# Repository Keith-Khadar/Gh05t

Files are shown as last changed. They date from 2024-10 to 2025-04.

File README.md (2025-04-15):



# Project Overview

This project aims to design and develop a wearable EEG headset with an integrated data acquisition system. Using OpenBCI Ultracortex Mark IV as a template, the headset is designed to map the electrodes according to the 10-20 system. We expand on this design by integrating our own 3D printed or button-snap electrodes for enhanced modularity. Additionally, we investigate various EEG data acquistion hardware options, varying in cost, precision, and usability, to enhance accessibility and modularity in EEG systems - ranging from off-the-shelf hardware to custom-designed PCBs and circuit designs. The hardware will communicate with a computer for analysis by a machine learning (ML) model to detect gestures or possible speech, with the possibility of integration into Virtual-Reality (VR) applications. Lastly, the system will feature a custom GUI, enabling users to visualize EEG data in real-time from the various custom hardware configurations we explore.

We provide various levels to users depending on cost, precision, and usability:

| Feature                     | High Performance Development Board[^1]    | Balanced Performance Board[^2]                | Low Cost EEG Filtering Circuit[^3]            |
| --------------------------- | ----------------------------------------- | --------------------------------------------- | --------------------------------------------- |
| **Number of Channels**      | 8\*                                       | 8\*                                           | 8                                             |
| **Resolution**              | 24-bit                                    | 24-bit                                        | 12-bit                                        |
| **Typical Sampling Rate**   | 250 Hz                                    | 250 Hz                                        | <33 Hz                                        |
| **ADC Chip**                | ADS1299-IPAG                              | ADS1299-IPAG                                  | Internal RPi Pico ADC                         |
| **Board**                   | EEG Development Board with ESP32-S3       | Custom PCB                                    | Custom breadboard/featherboard circuit        |
| **Microcontroller**         | XIAO ESP32-C6                             | DFRobot Firebeetle ESP32 32D                  | Raspberry Pi Pico W                           |
| **Connectivity**            | USB-C/Bluetooth/WiFi                      | Micro-USB/Bluetooth/WiFi                      | Micro-USB/WiFi                                |
| **Power Source**            | Battery/USB                               | Battery/USB                                   | Battery/USB                                   |
| **Battery Life**            | 8 hours                                   | -                                             | <1 hour                                       |
| **GUI Support**             | OpenBCI GUI                               | Custom GUI                                    | Custom GUI                                    |
| **Form Factor**             | Button Snap Electrodes w/ OpenBCI Headset | 3D printed Claw Electrodes w/ OpenBCI Headset | 3D printed Claw Electrodes w/ Custom Headband |
| **Communication Protocols** | SPI, ESPNOW, UART                         | SPI, BLE                                      | UDP WebSocket                                 |
| **Price**                   | ~$375                                     | ~$100                                         | ~$50                                          |

\* The ADS1299 has the capabilities to daisy chain, therefore expanding the channel number from 8 to 16 but it is not fully implemented on the custom PCB. Refer to the ADS1299 PCB folder for additional information.

[^1]: Refer to [High_Performance\README.md](https://github.com/Keith-Khadar/Gh05t/tree/main/High_Performance) for more information on the setup and specifics for the system.
[^2]: Refer to [Balanced_Performance\README.md](https://github.com/Keith-Khadar/Gh05t/tree/main/Balanced_Performance) for more information on the setup and specifics for the system.
[^3]: Refer to [Low_Cost\README.md](https://github.com/Keith-Khadar/Gh05t/tree/main/Low_Cost) for more information on the setup and specifics for the system.

## Completed Work/In Progress for Milestone Production Release

-   **Working Balanced Performance Pipeline (ADS1299 Breakout PCB)**: Eye blinks were detected successfully in the FFT and Time Series plots but was unable to receive consistent and robust results after each trial.
    -   Work in progress of doing trial and error to reproduce results.
-   **Housing Design for Balanced Performance Board (Breakout PCB)**: A CAD design of a housing unit for the ADS1299 Breakout PCB was completed.
-   **Receiver code optimization for the High Performance board**: The receiver code was optimized for better efficiency on the high-performance board by restructuring logic, minimizing redundant operations, and improving resource utilization.
-   **Optimizing Real Time Reading on the GUI**: Since eye blinks were successfully shown in the time series, the SDED, with the calibration of the delta and alpha variables, was able to successfully label with minimal latency the sample positions where the blinking occurred.
-   **EEG Game Application**: In order to expand the application of using the EEG data and detecting events like eye blinking, a VR and simple blinking game was created. A WebSocket host was created in the GUI and successfully broadcasts the SDED labels to any client to act as a controller for a game.
-   **Signal Preprocessing** : The EEG signal preprocessing pipeline is fully implemented, ensuring artifact removal, filtering, and independent component extraction before further processing. FastICA, InfoMax, NLMS and VSS-APA are implemented to extract information components from raw EEG signals in real-time.
-   **Event Detection/Prediction Model**: The EEG-based event detection pipeline and machine learning models have been developed to analyze real-time brain activity and infer motor function. NLMS, Batch-Wiener Filter and VSS-APA have been implemeted for predictions - Statistical Deviation Event Detection Model and Information Theoretic Learning Point Process Detection Models have been implemented for more sophisticed event flagging.

# Project Architecture

### <p align="center">**High Performance Development Board**[^1]</p>

| <div style="width:400px">Hardware Architecture & Wiring</div>  | Components  | Communication Protocols  |
| ----------------------- | ----------------------- | ----------------------- |
| High Performance Board | - OpenBCI 3D Headset Design<br> - Depth-adjustable spring loaded 3D printed assembly with metal snap electrodes provides good signal strength for EEG signals <br> - EEG ESP Development Board with ESP32-S3 <br> - XIAO ESP32-C6<br> - Protective case for the development board<br> | - SPI communication between ADS1299 chip and ESP32-S3<br> - ESP-NOW WiFi data transmission between Development Board and ESP32-C6<br> - UART serialized data transmission through USB-C connection between ESP32-C6 and computer receiver <br> |

-   **Software**
    -   Once the ESP32-C6 captures the incoming EEG data from the ESP32-S3, the UART data is captured through a python script and written to a file. The captured EEG data in this file can be viewed using OpenBCI GUI. The EEG data in this file will be feed to the machine learning model to draw inferences after analysis of the data.
    -   A python script is employed to label and timestamp the 8-channel EEG blinking data. This script facilitates the real-time processing and organization of the data, ensuring that each blink event is accurately marked with its corresponding timestamp for subsequent analysis.
    -   An end-to-end high-performance EEG pipeline leverages an ESP32 EEG board and ESP32-C6 to wirelessly transmit 8-channel, ultra-low-noise data at 250 samples/sec via ESP-NOW, enabling real-time processing in Python and visualization through OpenBCI GUI or a custom interface.
    <p align="center">
    data collection stages
    fft plot
    </p>

### <p align="center">**Balanced Performance Board**[^2]</p>

| <div style="width:450px">Hardware Architecture & Wiring</div>  | Components  | Communication |
| ----------------------- | ----------------------- | ----------------------- |
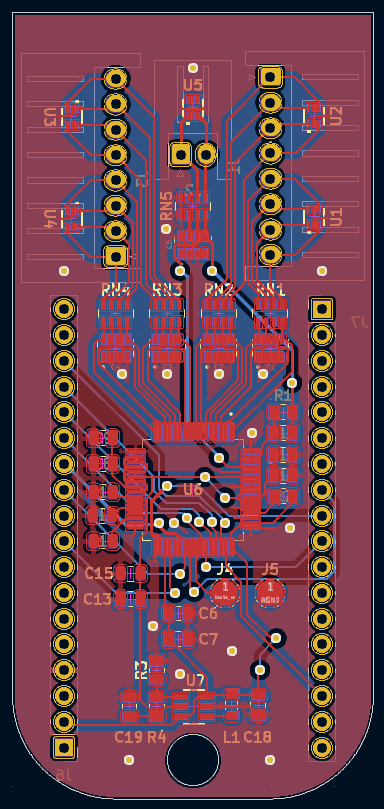
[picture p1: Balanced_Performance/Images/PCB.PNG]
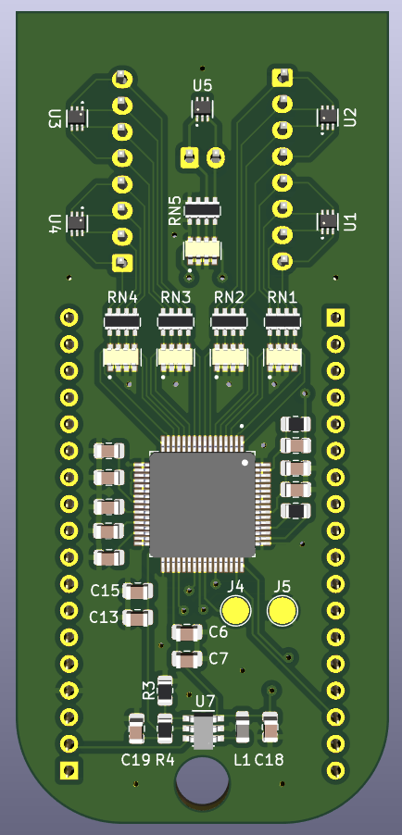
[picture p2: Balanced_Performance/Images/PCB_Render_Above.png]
|    | - OpenBCI 3D Headset Design<br> - 3D Printed Claw Electrodes<br> - Custom ADS1299 PCB<br> - DFRobot Firebeetle ESP32 32D <br> | - SPI communication between the ADS1299 PCB and Firebeetle ESP32 <br> - BLE data transmission between the Firebeetle ESP32 and computer receiver <br> |

-   **Software**
    -   Once the Firebeetle ESP32 is supplied power, the BLE server is turned on and ready to transmit data to any device that connects to the server. The **GH05T GUI** is used to connect to the BLE server and read incoming real-time data.

### <p align="center">**Low Cost Filtering Circuit**[^3]</p>

| <div style="width:500px">Hardware Architecture & Wiring</div>   | Components | Communication Protocols |
| ----------------------- | ----------------------- | ----------------------- |
|  | - Custom Filtering and Component Circuit on breadboard/featherboard <br> - Raspberry Pi Pico W <br> | - TCP WebSocket data transmission between Raspberry Pi Pico W and computer receiver |

-   **Software**
    -   Once the Raspberry Pi Pico W is supplied power,UDP WebSocket is opened and transmits data to any device that connects to the server. The **GH05T GUI** is used to connect to the WebSocket server and read incoming real-time data.

### <p align="center">**GH05T Graphic User Interface**[^4]</p>

| <div style="width:300px">Function and Feature Architecture</div> | Visuals/GUI  |
| ----------------| ---------------------- |
| GUI Flow | GUI Flow [PyQt](https://doc.qt.io/qtforpython-6/) & [Matplotlib](https://matplotlib.org/): Widget and EEG Data Visualization |

[^4]: Refer to [Gh05t GUI\README.md](https://github.com/Keith-Khadar/Gh05t/tree/main/Gh05t%20GUI) for more information on the setup and specifics on the GUI.

### <p align="center">**Signal Processing and Machine Learning**[^5]</p>

-   **EEG Signal Pre-processing**:

    -   Format:
        -   Input: Raw 4 channel electrode data
        -   Output: K-Independent Signals (Components)
    -   Processing Options:
        -   FastICA , NLMS: Fast Inference
        -   InfoMax or VSS-APA: Versatility & Robustness

-   **EEG Signal Machine Learning**:
    -   Format:
        -   Input: K-Independent Signals (Components)
        -   Output: User Defined Target Output
    -   Target:
        -   User Defined Target Desired Output, i.e. eye activity or motion.
    -   Model:
        -   Structure: Artifical Neural Network (Regressor)
        -   Pre-Training: PCA-Pretraining for optimal features
        -   Training: Network Tuning based on Target Data

[^5]: Refer to [Machine_Learning\README.md](https://github.com/Keith-Khadar/Gh05t/tree/main/Machine_Learning) for more information on the setup and specifics.

## Known Bugs

- The Balanced Performance Board ADS1299 completely stopped working after trying to fit the casing to the hardware. This was an unexpected issue that is not able to be understood. Possible issues that could have occurred for the chip to completely stop working is somehow the chip received a surge of power that could have damaged it. 

## Difficulties/Challenges

-   **3D Printing Fail**: Weak legs on 3D electrodes
    -   The initial model found and used for the electrodes has spindly legs. In combination with two snaps of the filament during printing, the legs were incredibly weak and many snapped during removal from the print bed.
    -   Fix: Load filament onto spool to eliminate snapping during print. Custom design electrodes with filleted legs to enhance their strength. Increase the number of walls when slicing model for printing.
    -   Above fix solved combined with printing on a higher quality printer and in a different orientation fixed the issues.
-   **Snap Plating**: Purchased snaps are covered in non-conductive coating
    -   Prevented soldering, but can be scrapped off with a knife.
    -   Reduces signal integritty of electrodes.
    -   Fix: Looking into alternative unplated snap connectors.
    -   Above fix solves the issue in initial testing. Will continue to monitor as further testing is conducted.
-   **Inaccurate EEG Data**: Data recorded during initial testing is inaccurate.
    -   The poor quality electrodes(see snap plating challenge & 3d printing fail) as well as the ADC optimized for Electromyography (EMG) data recording instead of the use case of Electroencephalography (EEG), resulted in poor quality data.
    -   Fix: Custom designed PCB breakout board for the ADS1299 which is designed for EEG data acquisition.
-   **GUI Real Time Data**: Optimizing the timing between data conversion from the ADS1299 to the GUI has introduced latency.
    -   Fix: Utilizing threading and precise timing between frame updating and loading.
-   **ADS1299 Electrode Setup**: Setting up the registers for specific BIAS, SRB1/2, and Electrode connections proved difficult with our system. This was causing reading alpha waves to be difficult.
    -   Fix: Using the SRB1, connected to the earlobe/mastoid, routed to all the negative parts of the electrode channels for reference. Using the BIAS, also connected to the earlobe/mastoid, routed to the postive electrode channels for signal derivation.

## License

## Contact

## Acknowledgements

We would like to extend our gratitude to OpenBCI for having open source repositories with headset designs, ADS1299 libraries, and user interface code. These repositories played a significant role in the success of the project!

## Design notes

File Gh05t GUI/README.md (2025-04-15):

# Real-Time EEG Visualization GUI
## Overview

The Graphic User Interface (GUI) is a Python-based real-time visualization tool for viewing multi-channel EEG data over Bluetooth from an ESP32 microcontroller. 

#### Features

- **Real-Time Data Visualization**: Plots live EEG data for multitude of channels in various formats: time, polar fft, and fft.
- **Various forms of data input**: The user has multiple data input options, allowing them flexibility to use various types of hardware.
- **Read Pre-recorded files**: The GUI supports edf and csv.
- **Customizable GUI**: Easy to adapt for additional features like saving data or adjusting plot parameters.
- **Export files**: Can export the incoming data.

#### Dependencies
1. **Hardware** (Optional)
    - **ADS1299 PCB**: Navigate to the esp32 folder, ```esp32\README.md```, for specific setup instructions for Firebeetle ESP32.
    - **Low Cost**: Navigate to the Low Cost folder, ```rpi_low_cost\gh0st\README.md```, for specific setup instructions for the RPi Pico W.
2. **Software**
    - Python 3.7+
    - Bluetooth support on host computer
3. **Libraries**
    - Refer to ```requirements.txt``` to install supporting Python libraries

## Setup Instructions

#### 1. Install Dependencies
Using the ```requirements.txt```, install the library dependencies required for the GUI to run for your environment.

#### 2. Run the GUI
Run the main script to start the GUI. The python script will scan for bluetooth devices automatically when the option is selected.

```bash
python main.py
```

#### 3*. (Optional) Connect to WebSocket Host
The GUI automatically opens the WebSocket at start up. It only broadcasts labels, which requires the user to enable the manual or ML labeling in order to start broadcasting the information. The WebSocket URL is shown to the user next to the Data Input button (the IP4 Addr of the local machine with the PORT number).

The WebSocket broadcasts the labels for the benefit of external applications. For more information, refer to ```Applications``` folder in the repository.

## Code Architecture

- **`main.py`**: Main script for the GUI.
- **`utils/`**: Folder containing all the helper classes and functions.
  - **`ble_handler_.py`**: Creates client to recieve incoming information from the ESP32 BLE server.
  - **`file_handler.py`**: Handles the file uploading, handling, and exporting for data. 
  - **`plot_manager.py`**: Plots various types of Graphs specified by the user.
  - **`signal_processing.py`**: Creates filters and applies signal processing to incoming data.
  - **`websocket_handler.py`**: Handles the websocket communication for the low cost hardware data input. 
- **`resource/`**: Contains any png or supporting files for the GUI
- **`example_eeg_data/`**: Includes eeg data that can be used to test the visualizer.
- **`data/`**: Holds the binary folder where the incoming data will be stored before export. Additionally can be a folder to hold an exported data files.
- **`test/`**: Contains all the unit testing for the GUI.
- **`requirements.txt`**: List of required Python libraries.

## GUI Navigation
The user first must specify how they are inputting data to be read. There are four options to the user for inputting data:
- **ADS1299 PCB**: This is if the user created their own PCB with the ADS1299 chip which communicates to a DFRobot Firebeetle ESP32 development board and sends the data via BLE.
- **Low Cost**: This is if the user does not have the ADS1299 and creates their own low cost breadboard/featherboard circuit that uses an external 12-bit ADC to communicate with the DFRobot Firebeetle ESP32 development to send data over BLE.
- **File Import**: If the user has no hardware to interface with, file import is supported for type .edf.



Once the data is imported, the user has the ability to add and remove plots from the visual. They can play or stop the incoming data stream to look closer at the plots. Additionally, there is a button to allow the user to export the data if they want to create a local file on their machine with the incoming data stream.

## Troubleshooting/Known Bugs
- None.

## Future Work
- The GUI can currently only read from .edf files when uploading. Future work would include expanding the capabilities to .dat and .txt files. 
- Add the ability to scrub through the data on a timeline.
- Package the GUI into a single .EXE once completed with features. This will be done with PyInstaller.

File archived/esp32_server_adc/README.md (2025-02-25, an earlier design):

# README for esp32_server_adc.ino
This project demonstrates a BLE (Bluetooth Low Energy) server application on the ESP32-C6 that reads analog data from a sensor connected to the `A0` pin and broadcasts 
the data to the connected BLE client (mobile phone). The server updates the BLE characteristic every 2 seconds, allowing connected device to retrieve the real-time 
analog value.

## Features
- Uses BLE to broadcast sensor data.
- Reads analog data from pin `A0` with a 12-bit resolution.
- Uses `nRF Connect` for viewing BLE data on mobile.

## Requirements
- **Hardware**: ESP32-C6 board
- **Software**: 
  - Arduino IDE with ESP32 board support
  - ESP32 BLE library (compatible with ESP32-C6)
  - Download nRFConnect app on the phone

## Setup Instructions
1. **Setting up ESP32 board option in the Arduino IDE** 
   - Open Preferences: Go to "File > Preferences" in the Arduino IDE. 
   - Add Board Manager URL: In the "Additional Board Manager URLs" field, paste the ESP32 URL 
     (usually "https://espressif.github.io/arduino-esp32/package_esp32_index.json"). 
   - Open Boards Manager: Navigate to "Tools > Board > Boards Manager". 
   - Install ESP32: Search for "ESP32" and click "Install" for the "ESP32 by Espressif Systems" option. 

2. **Open in Arduino IDE**
   - Open the `esp32_server_adc.ino` file in Arduino IDE.

3. **Upload the Code**
   - Connect your ESP32-C6 board via USB.
   - Click on the upload button to flash the code to the board.

## Code Overview
- **UUID Definitions**: Unique identifiers are used for the BLE service and characteristic.
- **Analog Pin**: Reads data from `A0` and sends it over BLE.
- **BLE Setup**:
  - Initializes BLE with the device name "XIAO_ESP32C6".
  - Creates a BLE server and starts a service with read and write properties.
  - The characteristic is updated with the analog sensor data every 2 seconds.

## BLE Structure

| Parameter      | Value                                    |
|----------------|------------------------------------------|
| **Service UUID**        | `4fafc201-1fb5-459e-8fcc-c5c9c331914b` |
| **Characteristic UUID** | `beb5483e-36e1-4688-b7f5-ea07361b26a8` |

For specific details, please refer to inline comments.

## Usage
1. After flashing, the ESP32-C6 will begin advertising.
2. Use the nRF Connect app to scan for devices.
3. Connect to `XIAO_ESP32C6`.
4. Read the characteristic value to view the analog data.

## Example Output
On connection, the BLE client will receive the analog values every 2 seconds. 
Sample output on the serial monitor:
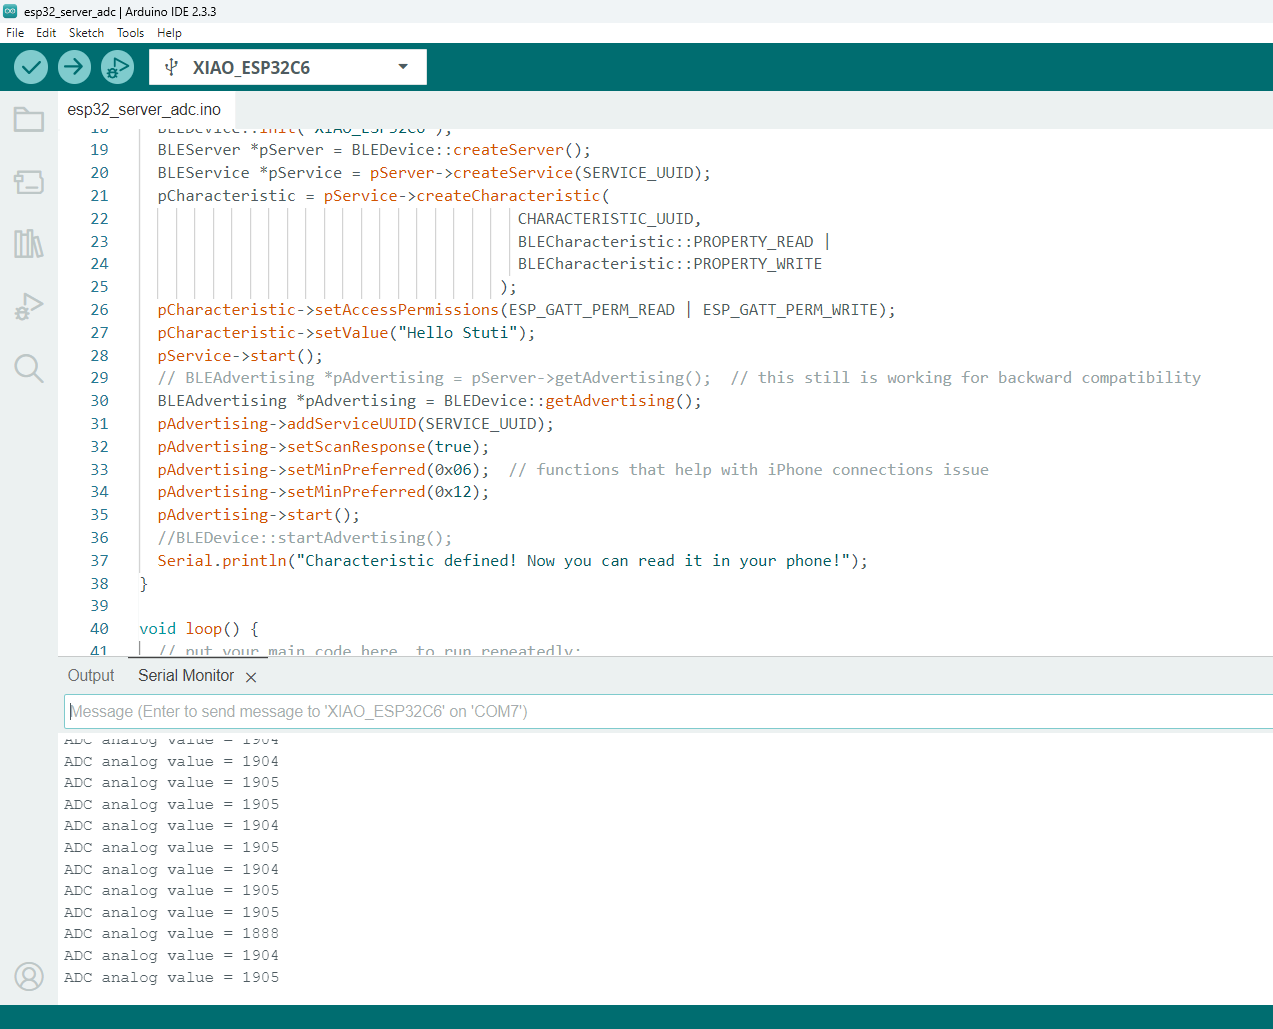
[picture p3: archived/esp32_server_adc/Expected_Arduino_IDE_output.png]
Arduino IDE output


Sample output on the nRF Connect app:<br>
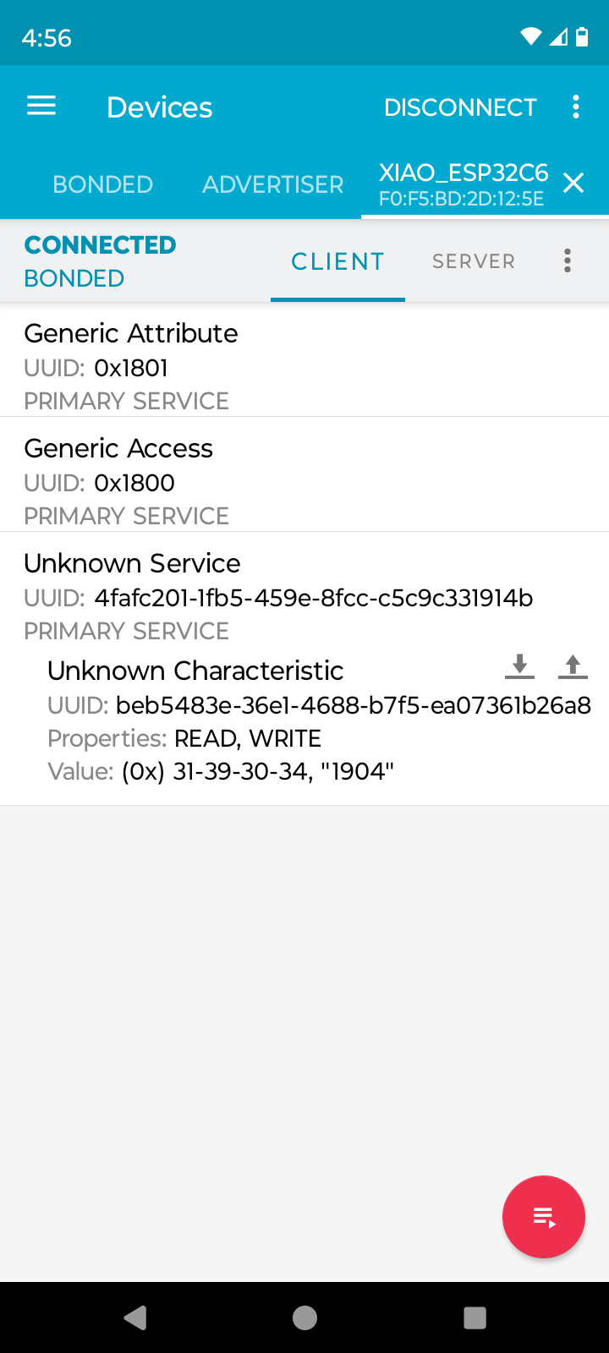
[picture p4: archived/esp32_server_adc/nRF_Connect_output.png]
nRF Connect output


## Mobile Interaction
Since this project utilizes Bluetooth Low Energy (BLE), users need to manually poll the mobile application to retrieve the latest ADC values. 

## Troubleshooting
- Ensure the ESP32-C6 board is selected and it is connected to the correct COM port.
- Check that the correct libraries have been installed in Arduino IDE.

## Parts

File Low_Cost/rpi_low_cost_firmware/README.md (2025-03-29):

# Installation
First you need to install circuit python on your Raspberry Pi Pico. You can do so here at this link: https://circuitpython.org/board/raspberry_pi_pico_w/

# Uploading our code to you Pico
Next you need to upload our code.py into your circuitpy drive that was created from installing circuit python onto your Pico. Afterwards you need to edit/create a settings.toml where you need to include some information.
You need the following information in your settings.toml 'CIRCUITPY_WIFI_SSID', 'CIRCUITPY_WIFI_PASSWORD', 'CIRCUITPY_MULTICAST_GROUP', 'CIRCUITPY_PORT', 'CIRCUITPY_RATE'.

# Using the code
Once you upload the code to the Pico you should be good to go. Now whenever you power the Pico it should create a wifi network with the name and password you specified in the settings.toml.
Once you connect to the wifi it should broadcast data to the ip specified in your mulitcast group and at the port specified in the settings.toml.

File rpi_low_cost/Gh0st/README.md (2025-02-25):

# Raspberry Pi Pico Project
## Overview
This is for the low cost version of the EEG project. It is written in C for the Raspberry Pi Pico. After flashing the firmware onto the Pico, it will output its IP address over serial communication at a baud rate of 115200. From there you can connect using a TCP websocket on port 4242.

## Prerequisites
Raspberry Pi Pico board
C/C++ SDK for the Pico (Raspberry Pi Pico SDK Setup Guide)
CMake (version 3.13 or later)
Make
Serial monitor (e.g., minicom, PuTTY, or Arduino Serial Monitor)
Setup Instructions
## Clone or Download the Code
Download or clone this repository to your local machine.

## Build the Project
Open a terminal and navigate to the project’s root directory:

```bash
cd Gh0st/rpi_low_cost/Gh0st/build
make
```
This will generate a .uf2 file in the build directory.

## Flash the Pico

Hold down the BOOTSEL button on the Pico.
While holding the button, plug the Pico into your computer via USB.
A new mass storage device named RPI-RP2 should appear.
Drag and drop the generated .uf2 file into the RPI-RP2 drive.
Once the file transfer is complete, the Pico will reboot automatically.
View Serial Output
To read the IP address output from the Pico:

Unplug and reconnect the Pico (without holding the BOOTSEL button).
Open your preferred serial monitor and connect to the appropriate port at a baud rate of 115200.
Example using minicom:

```bash
minicom -b 115200 -D /dev/ttyUSB0
(Replace /dev/ttyUSB0 with your actual serial port.)
```
The Pico should display its assigned IP address upon startup.

## Troubleshooting
If the RPI-RP2 drive doesn’t appear, ensure you’re holding the BOOTSEL button while plugging in the Pico.
If no serial output appears, double-check your serial port and baud rate settings.

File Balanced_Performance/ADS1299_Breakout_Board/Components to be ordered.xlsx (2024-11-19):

Component | Quantity (for one board) | Total quantity to be ordered * double the quantity for backup | Ordered? | Links | Price (based on total quantity) | Notes
TPD4E1B06 - Input protection IC | 6 | 24 | F | https://www.digikey.com/en/products/detail/texas-instruments/TPD4E1B06DRLR/4878711 | $8.16
TPS72325 - -2.5V Regulator |  |  |  | https://www.digikey.com/en/products/base-product/texas-instruments/296/TPS72325/23009
TLV700xx - +2.5V Regulator |  |  |  | https://www.digikey.com/en/products/detail/texas-instruments/TLV70033QDDCRQ1/2353662; https://www.mouser.com/c/semiconductors/power-management-ics/voltage-regulators-voltage-controllers/ldo-voltage-regulators/?m=Texas%20Instruments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
MCP1754T-3302E/OT - +3V Regulator |  |  |  | https://www.digikey.com/en/products/detail/microchip-technology/MCP1754T-3302E-OT/2775775; https://www.mouser.com/ProductDetail/Microchip-Technology/MCP1754T-3302E-OT?qs=3wWX5hyYeeTLQCcLPl0MGw%3D%3D
100 uF capacitor | 1 | 10 | F | https://www.digikey.com/en/products/detail/samsung-electro-mechanics/CL21A107MQYNNWE/16615644 | $6.70 | 6.3V rated
10µF capacitor | 1 | 100 | F | https://www.digikey.com/en/products/detail/venkel/C0805X5R100-106KNP-CT/14652235 | $3.84 | 10V rated
1 uF capacitor | 9 | 100 | F | https://www.digikey.com/en/products/detail/venkel/C0805X5R160-105KNE-CT/14651263 | $2.44 | 16V rated
0.1 uF capacitor | 2 | 100 | F | https://www.digikey.com/en/products/detail/venkel/C0805Z5U500-104MNP-CT/14651283 | $1.81 | 50V rated
1 nF capacitor | 1 | 100 | F | https://www.digikey.com/en/products/detail/venkel/C0805X7R250-102KNP-CT/14651672 | 1.81 | 25V rated
1000pF (4 pack) ceramic capacitor | 5 | 50 | F | https://www.digikey.com/en/products/detail/kyocera-avx/W3A45C102K4T2A/9948514 | $6.41 | 50V rated
2.2k (4 pack) resistors | 5 | 50 | F | https://www.digikey.sg/en/products/detail/bourns-inc/CAY16-2201F4LF/2566534 | $1.79
1M resistor | 1 | 100 | F | https://www.digikey.com/en/products/detail/venkel/AGCR0805-RK-1004FT-CT/21345893 | $1.78
Rechargable battery
Crystal oscillator
ADS1299-IPAG | 1 |  | T | https://www.ti.com/product/ADS1299 | $41.58
JST Female connectors 8 Pin |  |  | T | https://www.amazon.com/Kidisoii-Connector-Header-Adapter-XH2-5-DIP-R/dp/B0CXMYPVNL
 |  | https://www.digikey.com/en/products/filter/-capacitors/59 |  |  |  | Link to OpenBCI, Cyton board part list
 |  |  |  |  |  | https://github.com/OpenBCI/V3_Hardware_Design_Files/blob/master/OpenBCI%20Cyton%20Designs/OBCI_Cyton_Plots/OBCI_V4_C%20(Component%20Positions).txt

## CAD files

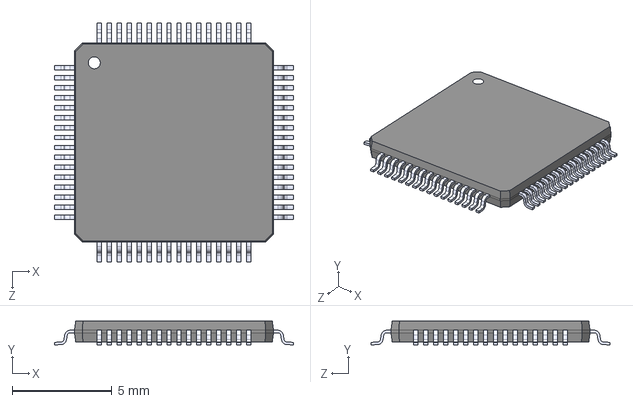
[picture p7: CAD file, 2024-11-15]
Balanced_Performance/ADS1299_Breakout_Board/KiCad_Lib/ADS1299/ADS1299IPAG.step
12.0 x 1.20 x 12.0 mm

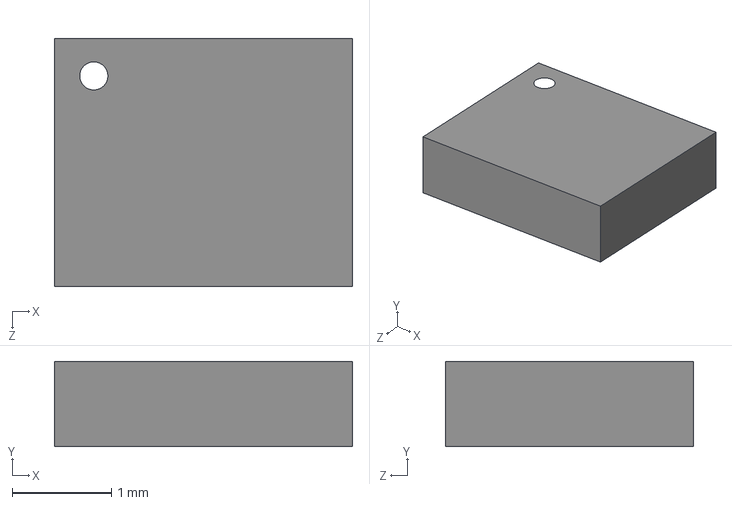
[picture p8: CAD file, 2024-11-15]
Balanced_Performance/ADS1299_Breakout_Board/KiCad_Lib/LSM6DSOX/LSM6DSOX.step
3.00 x 0.86 x 2.50 mm

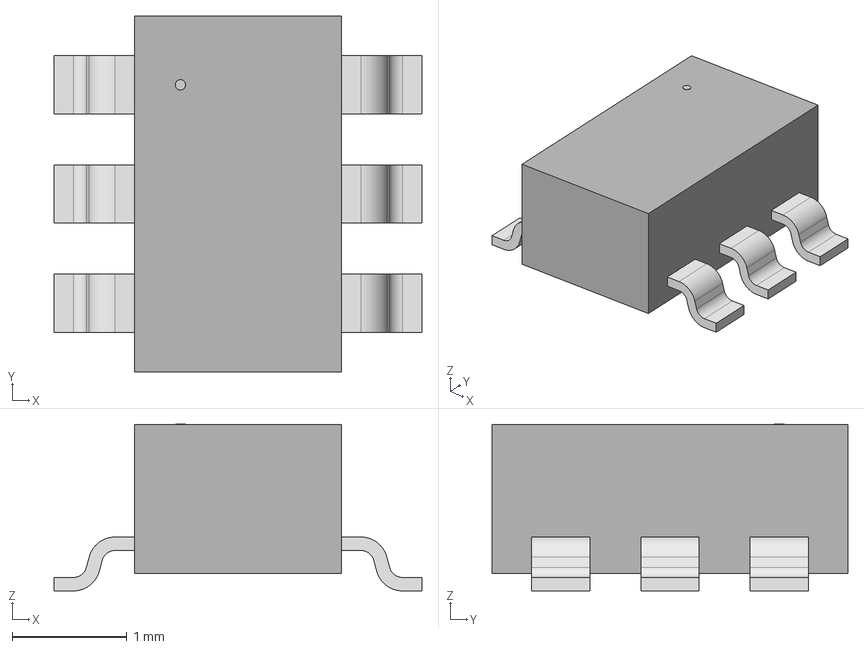
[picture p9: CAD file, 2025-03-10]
Balanced_Performance/Balanced_PCB/ProjectLibraries/MCP1640/MCP1640.step
3.20 x 3.10 x 1.45 mm

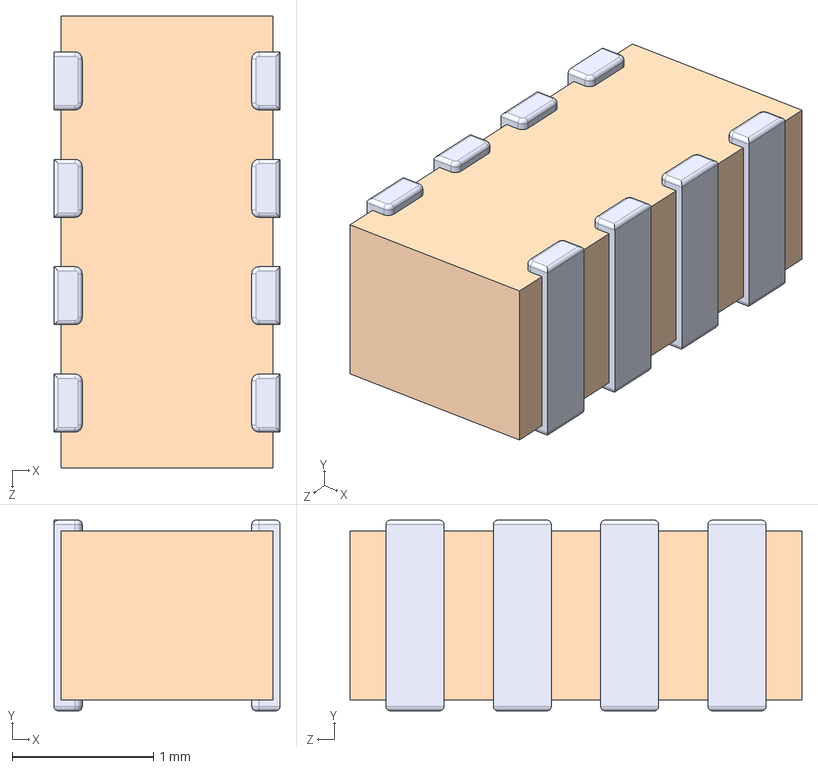
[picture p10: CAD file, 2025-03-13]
Balanced_Performance/Balanced_PCB/ProjectLibraries/W3A45C102K4T2A/W3A45C102K4T2A.step
1.60 x 1.35 x 3.20 mm

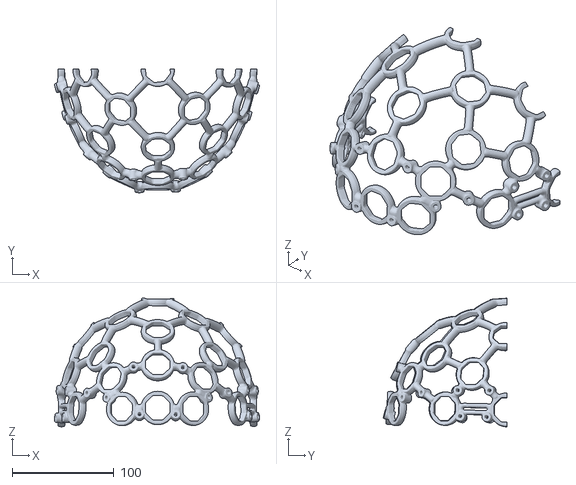
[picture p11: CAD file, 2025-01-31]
Balanced_Performance/CAD/EEG Headset/medium_headset_front_half.stl
201.0 x 121.2 x 126.2

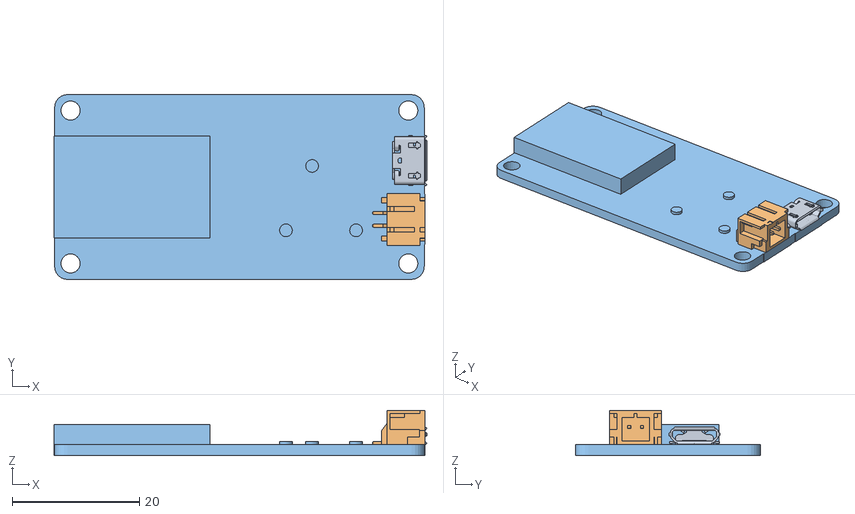
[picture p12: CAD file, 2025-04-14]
Balanced_Performance/CAD/HousingBad/ESP32_Firebeetle_DFR0478V4 v6.obj
58.5 x 29.0 x 7.08
WiFi

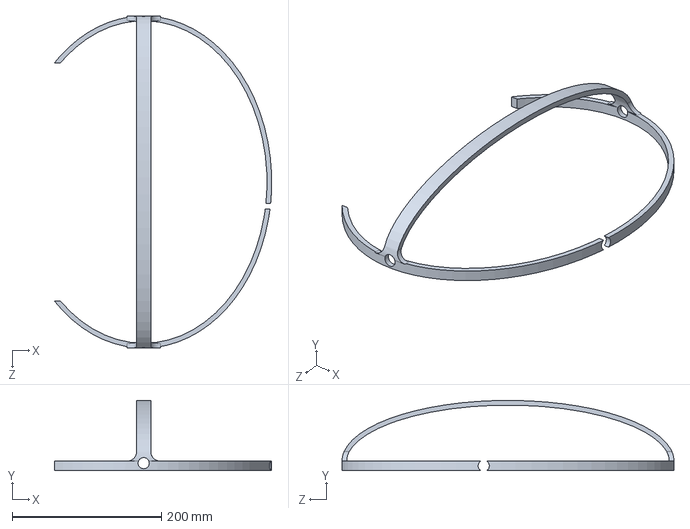
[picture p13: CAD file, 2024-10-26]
hardware/cad/head-mount/proto1.SLDPRT
290.8 x 93.9 x 444.5 mm

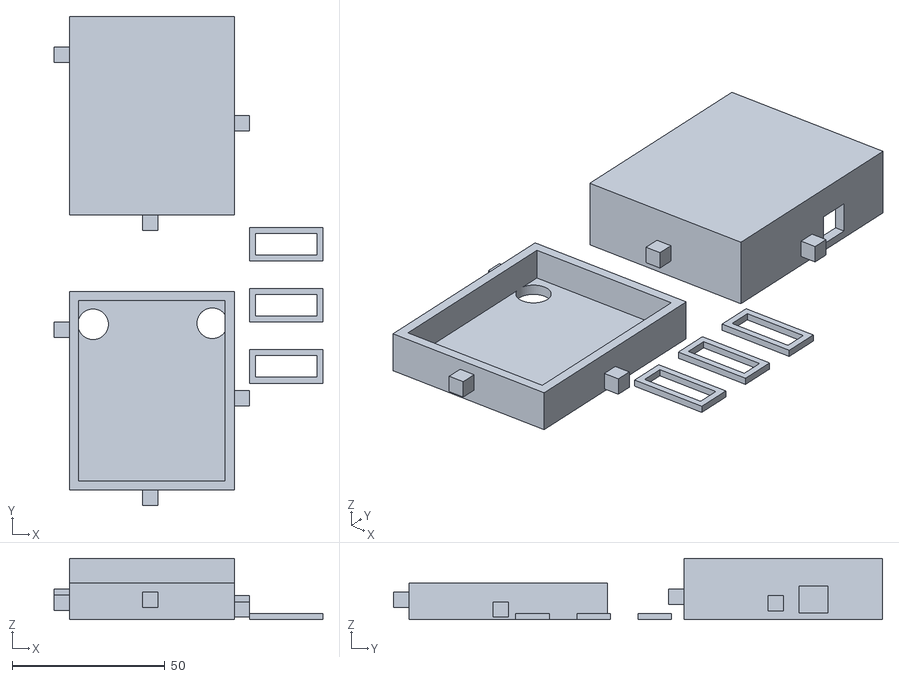
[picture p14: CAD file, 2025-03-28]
High_Performance/CAD/high_performance_board_case.stl
88.0 x 160.0 x 20.0

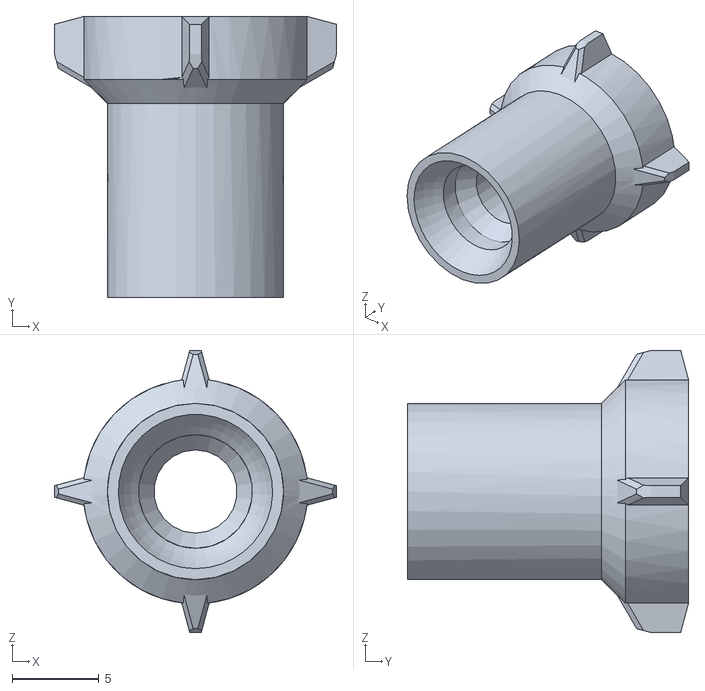
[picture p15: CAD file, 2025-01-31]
Balanced_Performance/CAD/EEG Headset/electrode_holder.STL
16.3 x 16.2 x 16.3

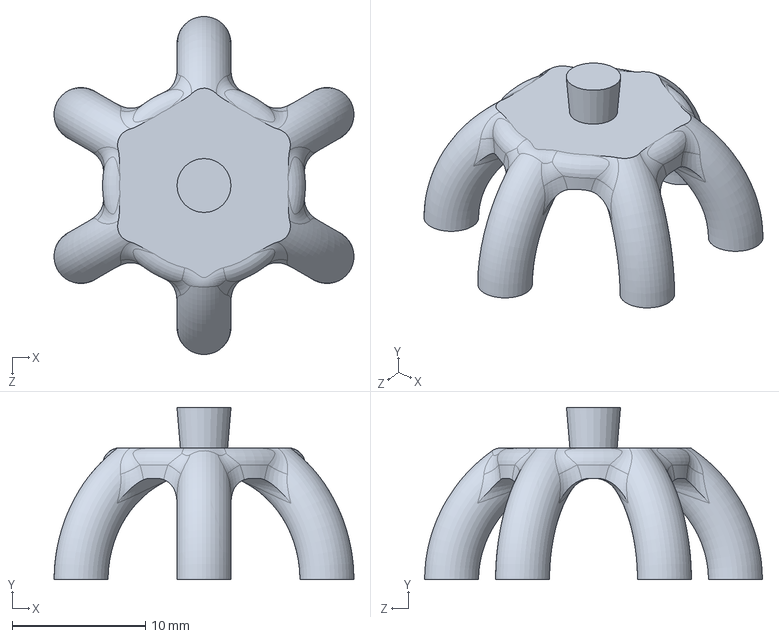
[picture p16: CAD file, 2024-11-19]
Balanced_Performance/CAD/Electrode/electrode.SLDPRT
22.5 x 13.0 x 25.4 mm

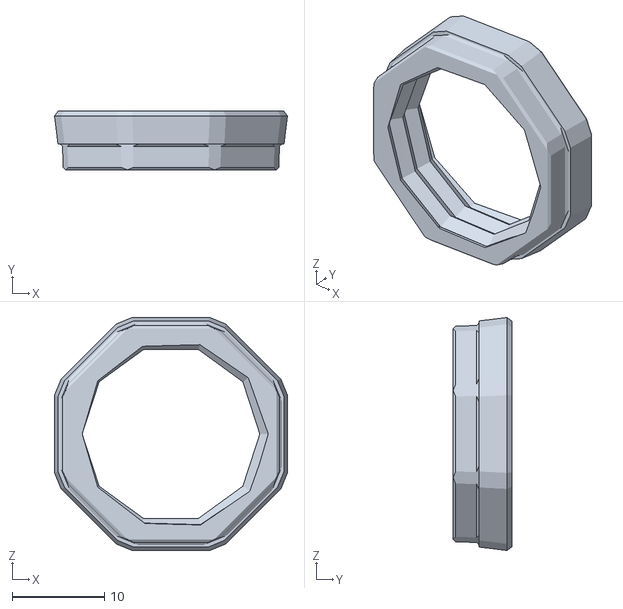
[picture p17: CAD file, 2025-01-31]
Balanced_Performance/CAD/EEG Headset/hexagonal_fitting.STL
25.3 x 6.35 x 25.3

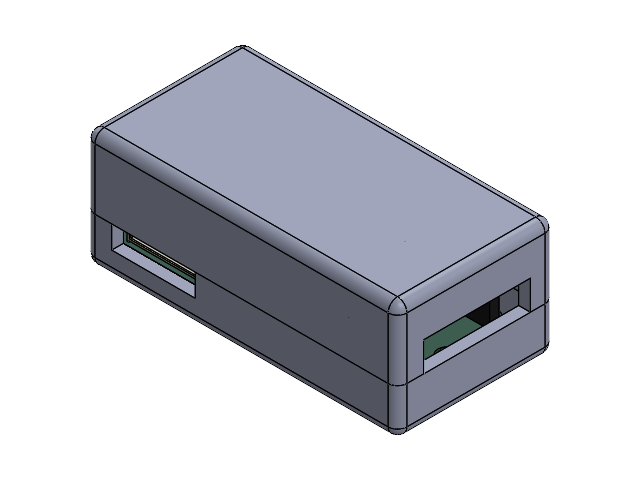
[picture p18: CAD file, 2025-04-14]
Balanced_Performance/CAD/Housing/Balanced_PCB_Housing.SLDASM
Balanced_PCB_Housing
SOT_563.step x 5
C_0805_2012Metric-0.step x 14
W3A45C102KAT2A.step x 5
L_0805_2012Metric-1.step
R_Array_Concave_4x0603-2.step x 5
R_0805_2012Metric-3.step x 4
PAG64.step
part.step
PinSocket_1x18_P2.54mm_Vertical-4.step x 2
JST_S2B_XH_A.step
JST_S8B_XH_A.step x 2
Combined_PCB_PCB.step

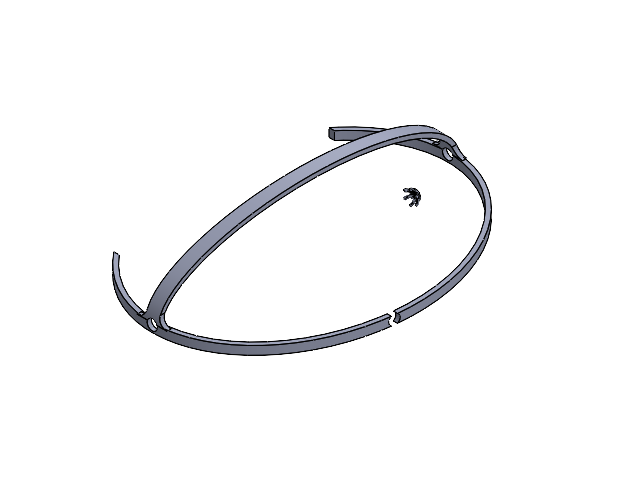
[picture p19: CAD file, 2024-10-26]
hardware/cad/hat.SLDASM
proto1
conductive electrode-short finger-not ours x 2

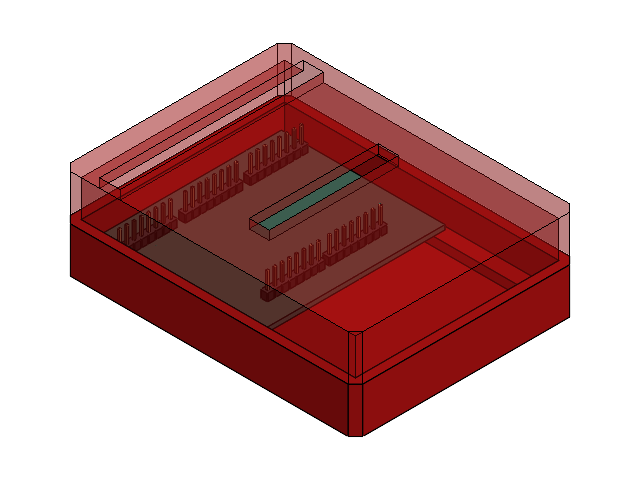
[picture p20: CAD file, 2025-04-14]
Balanced_Performance/CAD/Housing/ADS1299_Breakout_Board_Housing.SLDASM
ADS1299_Breakout_Board_Housing
PinHeader_1x08_P254mm_Vertical.step x 5
ADS1299_Breakout_Board_PCB.step

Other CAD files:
Balanced_Performance/CAD/Electrode/conductive electrode-short finger-not ours.SLDPRT
Balanced_Performance/CAD/HousingBad/ESP32_Firebeetle_DFR0478V4 v7.iges
Balanced_Performance/CAD/EEG Headset/fastening_screw.STL
Balanced_Performance/CAD/EEG Headset/medium_headset_back_half.stl
Balanced_Performance/CAD/EEG Headset/wire_clip.stl
Balanced_Performance/CAD/Electrode/conductive electrode-short finger-not ours.stl
Balanced_Performance/CAD/Electrode/electrode.STL
Balanced_Performance/CAD/Electrode/electrode_screw.SLDPRT
Balanced_Performance/CAD/Electrode/electrode_screw.STL
Balanced_Performance/CAD/Housing/ADS1299_Breakout_Board.SLDASM
Balanced_Performance/CAD/Housing/ADS1299_Breakout_Board.step
Balanced_Performance/CAD/Housing/ADS1299_Breakout_Board_Housing.SLDPRT
Balanced_Performance/CAD/Housing/Balanced_PCB.SLDASM
Balanced_Performance/CAD/Housing/Balanced_PCB.step
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

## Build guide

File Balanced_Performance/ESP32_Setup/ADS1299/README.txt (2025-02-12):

This Library opens communication between ESP32 and the ADS1299
SPI register fuses are directly set to match the ADS1299 interface requirements.
SCK rates: 1MHz, 4MHz, 8MHz. 
All registers and commands are fully accessable.
Here is a list of the functions and parameters available from the Library.

ADS1299.Initialize(int _DRDY, int _RST, int _CS, int _FREQ)
	Data Ready pin, Chip Select pin, and SCK frequency in MHz.
	the current shield uses DRDY = 8; RST 9 CS = 10.
	frequency options are 1MHz, 4MHz, 8MHz.
	bear in mind that at higher frequencies, appropriate delays
	must be taken when sending multiple bytes (DS p.37)
	initialization performs recommended timing and toggle of /RESET pin

//Public Variables

    int DRDY, CS; 		// pin numbers for DRDY and CS 
	These are part of the constructor
	they are not implemented in the current library
	but could be useful in future member functions

    int stat;			// used to hold the status register
	the status register is the first byte returned when you read channel data
	it has 1100 + LOFF_STATP + LOFF_STATN + GPIO[7:4]

    byte regData [24];		// array is used to mirror register data
	this array is used to write multiple locations of ADS register data using WREGS()
	user must first assign target values to the corresponding locations in regData aray
	a call to RREGS() will read multiple locations and update regData array
  
    long channelData [9];	// array used when reading channel data
    boolean verbose;		// turn on/off Serial feedback

//System Commands   

    void WAKEUP();	// wakeup from standby mode
    void STANDBY();	// go into standby mode
    void RESET();	// reset all registers to default values
    void START();	// start a data conversion session
    void STOP();	// stop data conversion

	timed delays are taken where required in the above funcitons. 
	bear in mind the timing of your byte to byte transmission.
	clk on ADS is ~2MHz, so that is a limit.
    
//Data Read Commands

    void RDATAC();	
	enter Read Data Continuous mode
	Read Data Continuous mode enables the ADC and shift registers
	in this mode, you can start a sampling session by setting the start pin,
	or sending the start command

    void SDATAC();	
	enter Stop Read Data Continuous mode
	this mode will let you write and read registers

    void RDATA();	
	Read Data command is used when you're in Stop Read Data Continuous mode
	if you send or set the 'start' command, this allows you to sample on DRDY
	and also have access to read/write the registers. see DS p.37 
    
//Register Read/Write Commands	

    byte getDeviceID();
	simple hello world to check that the device is working properly
	returns 0x3E on the Dev Module I'm using.
	must be in Stop Data Continuous mode prior to sending this

    byte RREG(byte _address);
	returns the value of one register address, specified
	the funcion also updates regData at _address

    void RREGS(byte _address, byte _numRegistersMinusOne);     
	updates the public regData array with current values
	_address is the address to start reading at
	_numRegistersMinusOne is the number of registers to read past the _address
	NOTE: the public regData array behaves like a mirror of the ADS internal arrays,
	however, the user must update the mirror. 

    void printRegisterName(byte _address);
	this is a look up table. part of the verbose feedback and not used external to the library

    void WREG(byte _address, byte _value); 
	writes a single value specified by _value to the register address at _address.

    void WREGS(byte _address, byte _numRegistersMinusOne); 
	writes a number of values to sequential addresses starting at _address
	user must first set values in correct locations of the public byte array regData
	regData is a mirror of the ADS register values

    void printHex(byte _data);
	used to streamline verbose feedback 

    void updateChannelData();
	the public array, channelData[8] gets updated, along with the status register.
	there is bitwise conversion from 3 byte 2's compliment to 4 byte 2's compliment (long)
    
//SPI Transfer function

    byte transfer(byte _data);
	puts the byte _data on the SPI bus, and returns a byte from the SPI bus.

//KNOWN ISSUES

	verbose feedback in the updateChannelData() function bumps against the DRDY signal
	this is because 115200 baud can't keep up?

//USING THIS LIBRARY
	
	The START pin is not broken out. You must send the START() command instead.
	For daisy-chaining in the future, we will route a GPIO to the START pin and 
	header socket.

	You must remeber to get out of Read Data Continuous mode if you want 
	to read/write, and do other register things.

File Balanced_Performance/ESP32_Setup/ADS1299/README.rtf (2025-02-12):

Texas Instruments ADS1299 Arduino Library

This folder contains all work and research for the creation of a software bridge between the Texas Instruments ADS1299 EEG/ECG chip and an Arduino.

Hardware References
[1] ADS1299: http://www.ti.com/product/ads1299
[2] ADS1299 Datasheet: http://www.ti.com/lit/ds/sbas499a/sbas499a.pdf
[3] ADS1299 Analog Evaluation Module: http://www.ti.com/lit/ug/slau443/slau443.pdf

Files
ADS2199.h - Arduino library header file
- contains class methods/variables
ADS1299.cpp - Arduino library cpp file
- contains content of methods and references to the page numbers in the above documents
- current methods:
- WAKEUP()
- STANDBY()
- RESET()
- START()
- STOP()
- RDATAC() - read data continuous
- SDATAC() - stop data continuous
- RDATA()
- RREG()
- WREG()
- transfer() - SPI bit transfer
- updateData() - print data from ADS1299 to serial monitor in Arduino IDE
Definitions.h - Contains all of the variable definitions that are relevant to the ADS1299 chip commands and the SPI communication between the chip and the Arduino.
examples/example_2 - an example arduino sketch that show you how to use the currently implemented methods of the library
keywords.txt - defines the keywords that change color automatically in an arduino sketch using this library

Extra Materials
The "reference" folder contains websites that contain relevant information to the development of the code and also options for electrodes and circuit design of active electrodes and other open-source EEG tools.
Links from meeting with Sean Montgomery (from Sensorstar Labs):
- https://www.olimex.com/Products/EEG/OpenEEG/EEG-ANALOG-ASM/
- https://www.olimex.com/Products/EEG/Electrodes/
- https://www.olimex.com/Products/EEG/Electrodes/EEG-AE/
- https://www.olimex.com/Products/EEG/OpenEEG/EEG-SMT/resources/EEG-SMT-SCHEMATIC-REV-B.pdf
- Sean's Website: http://produceconsumerobot.com/biosensing/
- http://www.saelig.com/miva/merchant.mvc?
- http://www.saelig.com/miva/merchant.mvc?
- http://www.saelig.com/supplier/plessey/PS25255.pdf
- http://ieeexplore.ieee.org/xpl/login.jsp?tp=&arnumber=5598518&url=http%3A%2F%2Fieeexplore.ieee.org%2Fxpls%2Fabs_all.jsp%3Farnumber%3D5598518

version 1) developed by Conor Russomanno (6/20/13)

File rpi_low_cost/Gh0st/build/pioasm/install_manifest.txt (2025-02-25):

/home/embedded/pico/Gh0st/build/pioasm-install/pioasm/pioasm
/home/embedded/pico/Gh0st/build/pioasm-install/pioasm/pioasmTargets.cmake
/home/embedded/pico/Gh0st/build/pioasm-install/pioasm/pioasmTargets-release.cmake
/home/embedded/pico/Gh0st/build/pioasm-install/pioasm/pioasmConfig.cmake
/home/embedded/pico/Gh0st/build/pioasm-install/pioasm/pioasmConfigVersion.cmake

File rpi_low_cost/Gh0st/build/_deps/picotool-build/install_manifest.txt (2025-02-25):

/home/embedded/pico/Gh0st/build/_deps/picotool/picotool
/home/embedded/pico/Gh0st/build/_deps/picotool/picotoolTargets.cmake
/home/embedded/pico/Gh0st/build/_deps/picotool/picotoolTargets-release.cmake
/home/embedded/pico/Gh0st/build/_deps/picotool/picotoolConfig.cmake
/home/embedded/pico/Gh0st/build/_deps/picotool/picotoolConfigVersion.cmake

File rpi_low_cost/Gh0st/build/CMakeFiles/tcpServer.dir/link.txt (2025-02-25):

/usr/bin/arm-none-eabi-g++ -mcpu=cortex-m0plus -mthumb -g -O3 -DNDEBUG -Wl,--build-id=none -Wl,-Map=tcpServer.elf.map --specs=nosys.specs -Wl,--wrap=__clzsi2 -Wl,--wrap=__clzdi2 -Wl,--wrap=__ctzsi2 -Wl,--wrap=__popcountsi2 -Wl,--wrap=__popcountdi2 -Wl,--wrap=__clz -Wl,--wrap=__clzl -Wl,--wrap=__clzll -Wl,--wrap=__ctzdi2 -Wl,--wrap=__aeabi_idiv -Wl,--wrap=__aeabi_idivmod -Wl,--wrap=__aeabi_ldivmod -Wl,--wrap=__aeabi_uidiv -Wl,--wrap=__aeabi_uidivmod -Wl,--wrap=__aeabi_uldivmod -Wl,--wrap=__aeabi_dadd -Wl,--wrap=__aeabi_ddiv -Wl,--wrap=__aeabi_dmul -Wl,--wrap=__aeabi_drsub -Wl,--wrap=__aeabi_dsub -Wl,--wrap=__aeabi_cdcmpeq -Wl,--wrap=__aeabi_cdrcmple -Wl,--wrap=__aeabi_cdcmple -Wl,--wrap=__aeabi_dcmpeq -Wl,--wrap=__aeabi_dcmplt -Wl,--wrap=__aeabi_dcmple -Wl,--wrap=__aeabi_dcmpge -Wl,--wrap=__aeabi_dcmpgt -Wl,--wrap=__aeabi_dcmpun -Wl,--wrap=__aeabi_i2d -Wl,--wrap=__aeabi_l2d -Wl,--wrap=__aeabi_ui2d -Wl,--wrap=__aeabi_ul2d -Wl,--wrap=__aeabi_d2iz -Wl,--wrap=__aeabi_d2lz -Wl,--wrap=__aeabi_d2uiz -Wl,--wrap=__aeabi_d2ulz -Wl,--wrap=__aeabi_d2f -Wl,--wrap=sqrt -Wl,--wrap=cos -Wl,--wrap=sin -Wl,--wrap=tan -Wl,--wrap=atan2 -Wl,--wrap=exp -Wl,--wrap=log -Wl,--wrap=ldexp -Wl,--wrap=copysign -Wl,--wrap=trunc -Wl,--wrap=floor -Wl,--wrap=ceil -Wl,--wrap=round -Wl,--wrap=sincos -Wl,--wrap=asin -Wl,--wrap=acos -Wl,--wrap=atan -Wl,--wrap=sinh -Wl,--wrap=cosh -Wl,--wrap=tanh -Wl,--wrap=asinh -Wl,--wrap=acosh -Wl,--wrap=atanh -Wl,--wrap=exp2 -Wl,--wrap=log2 -Wl,--wrap=exp10 -Wl,--wrap=log10 -Wl,--wrap=pow -Wl,--wrap=powint -Wl,--wrap=hypot -Wl,--wrap=cbrt -Wl,--wrap=fmod -Wl,--wrap=drem -Wl,--wrap=remainder -Wl,--wrap=remquo -Wl,--wrap=expm1 -Wl,--wrap=log1p -Wl,--wrap=fma -Wl,--wrap=__aeabi_lmul -Wl,--wrap=__aeabi_fadd -Wl,--wrap=__aeabi_fdiv -Wl,--wrap=__aeabi_fmul -Wl,--wrap=__aeabi_frsub -Wl,--wrap=__aeabi_fsub -Wl,--wrap=__aeabi_cfcmpeq -Wl,--wrap=__aeabi_cfrcmple -Wl,--wrap=__aeabi_cfcmple -Wl,--wrap=__aeabi_fcmpeq -Wl,--wrap=__aeabi_fcmplt -Wl,--wrap=__aeabi_fcmple -Wl,--wrap=__aeabi_fcmpge -Wl,--wrap=__aeabi_fcmpgt -Wl,--wrap=__aeabi_fcmpun -Wl,--wrap=__aeabi_i2f -Wl,--wrap=__aeabi_l2f -Wl,--wrap=__aeabi_ui2f -Wl,--wrap=__aeabi_ul2f -Wl,--wrap=__aeabi_f2iz -Wl,--wrap=__aeabi_f2lz -Wl,--wrap=__aeabi_f2uiz -Wl,--wrap=__aeabi_f2ulz -Wl,--wrap=__aeabi_f2d -Wl,--wrap=sqrtf -Wl,--wrap=cosf -Wl,--wrap=sinf -Wl,--wrap=tanf -Wl,--wrap=atan2f -Wl,--wrap=expf -Wl,--wrap=logf -Wl,--wrap=ldexpf -Wl,--wrap=copysignf -Wl,--wrap=truncf -Wl,--wrap=floorf -Wl,--wrap=ceilf -Wl,--wrap=roundf -Wl,--wrap=sincosf -Wl,--wrap=asinf -Wl,--wrap=acosf -Wl,--wrap=atanf -Wl,--wrap=sinhf -Wl,--wrap=coshf -Wl,--wrap=tanhf -Wl,--wrap=asinhf -Wl,--wrap=acoshf -Wl,--wrap=atanhf -Wl,--wrap=exp2f -Wl,--wrap=log2f -Wl,--wrap=exp10f -Wl,--wrap=log10f -Wl,--wrap=powf -Wl,--wrap=powintf -Wl,--wrap=hypotf -Wl,--wrap=cbrtf -Wl,--wrap=fmodf -Wl,--wrap=dremf -Wl,--wrap=remainderf -Wl,--wrap=remquof -Wl,--wrap=expm1f -Wl,--wrap=log1pf -Wl,--wrap=fmaf -Wl,--wrap=malloc -Wl,--wrap=calloc -Wl,--wrap=realloc -Wl,--wrap=free -Wl,--wrap=memcpy -Wl,--wrap=memset -Wl,--wrap=__aeabi_memcpy -Wl,--wrap=__aeabi_memset -Wl,--wrap=__aeabi_memcpy4 -Wl,--wrap=__aeabi_memset4 -Wl,--wrap=__aeabi_memcpy8 -Wl,--wrap=__aeabi_memset8 -Wl,-L/home/embedded/pico/Gh0st/build -Wl,--script=/home/embedded/pico/pico-sdk/src/rp2_common/pico_crt0/rp2040/memmap_default.ld -Wl,-z,max-page-size=4096 -Wl,--gc-sections -Wl,--no-warn-rwx-segments -Wl,--wrap=sprintf -Wl,--wrap=snprintf -Wl,--wrap=vsnprintf -Wl,--wrap=printf -Wl,--wrap=vprintf -Wl,--wrap=puts -Wl,--wrap=putchar -Wl,--wrap=getchar CMakeFiles/tcpServer.dir/main.c.o "CMakeFiles/tcpServer.dir/home/embedded/pico/pico-sdk/src/rp2_common/pico_lwip/lwip_nosys.c.o" "CMakeFiles/tcpServer.dir/home/embedded/pico/pico-sdk/src/rp2_common/pico_async_context/async_context_base.c.o" "CMakeFiles/tcpServer.dir/home/embedded/pico/pico-sdk/src/rp2040/pico_platform/platform.c.o" "CMakeFiles/tcpServer.dir/home/embedded/pico/pico-sdk/src/rp2_common/pico_platform_panic/panic.c.o" "CMakeFiles/tcpServer.dir/home/embedded/pico/pico-sdk/src/rp2_common/pico_rand/rand.c.o" "CMakeFiles/tcpServer.dir/home/embedded/pico/pico-sdk/src/rp2_common/pico_unique_id/unique_id.c.o" "CMakeFiles/tcpServer.dir/home/embedded/pico/pico-sdk/src/rp2_common/hardware_flash/flash.c.o" "CMakeFiles/tcpServer.dir/home/embedded/pico/pico-sdk/src/common/hardware_claim/claim.c.o" "CMakeFiles/tcpServer.dir/home/embedded/pico/pico-sdk/src/rp2_common/hardware_sync/sync.c.o" "CMakeFiles/tcpServer.dir/home/embedded/pico/pico-sdk/src/rp2_common/hardware_sync_spin_lock/sync_spin_lock.c.o" "CMakeFiles/tcpServer.dir/home/embedded/pico/pico-sdk/src/rp2_common/pico_bootrom/bootrom.c.o" "CMakeFiles/tcpServer.dir/home/embedded/pico/pico-sdk/src/rp2_common/pico_bootrom/bootrom_lock.c.o" "CMakeFiles/tcpServer.dir/home/embedded/pico/pico-sdk/src/rp2_common/hardware_boot_lock/boot_lock.c.o" "CMakeFiles/tcpServer.dir/home/embedded/pico/pico-sdk/src/rp2_common/pico_flash/flash.c.o" "CMakeFiles/tcpServer.dir/home/embedded/pico/pico-sdk/src/common/pico_time/time.c.o" "CMakeFiles/tcpServer.dir/home/embedded/pico/pico-sdk/src/common/pico_time/timeout_helper.c.o" "CMakeFiles/tcpServer.dir/home/embedded/pico/pico-sdk/src/rp2_common/hardware_timer/timer.c.o" "CMakeFiles/tcpServer.dir/home/embedded/pico/pico-sdk/src/rp2_common/hardware_irq/irq.c.o" "CMakeFiles/tcpServer.dir/home/embedded/pico/pico-sdk/src/rp2_common/hardware_irq/irq_handler_chain.S.o" "CMakeFiles/tcpServer.dir/home/embedded/pico/pico-sdk/src/common/pico_sync/sem.c.o" "CMakeFiles/tcpServer.dir/home/embedded/pico/pico-sdk/src/common/pico_sync/lock_core.c.o" "CMakeFiles/tcpServer.dir/home/embedded/pico/pico-sdk/src/common/pico_sync/mutex.c.o" "CMakeFiles/tcpServer.dir/home/embedded/pico/pico-sdk/src/common/pico_sync/critical_section.c.o" "CMakeFiles/tcpServer.dir/home/embedded/pico/pico-sdk/src/common/pico_util/datetime.c.o" "CMakeFiles/tcpServer.dir/home/embedded/pico/pico-sdk/src/common/pico_util/pheap.c.o" "CMakeFiles/tcpServer.dir/home/embedded/pico/pico-sdk/src/common/pico_util/queue.c.o" "CMakeFiles/tcpServer.dir/home/embedded/pico/pico-sdk/src/rp2_common/hardware_xip_cache/xip_cache.c.o" "CMakeFiles/tcpServer.dir/home/embedded/pico/pico-sdk/src/rp2_common/hardware_clocks/clocks.c.o" "CMakeFiles/tcpServer.dir/home/embedded/pico/pico-sdk/src/rp2_common/hardware_gpio/gpio.c.o" "CMakeFiles/tcpServer.dir/home/embedded/pico/pico-sdk/src/rp2_common/hardware_pll/pll.c.o" "CMakeFiles/tcpServer.dir/home/embedded/pico/pico-sdk/src/rp2_common/hardware_vreg/vreg.c.o" "CMakeFiles/tcpServer.dir/home/embedded/pico/pico-sdk/src/rp2_common/hardware_watchdog/watchdog.c.o" "CMakeFiles/tcpServer.dir/home/embedded/pico/pico-sdk/src/rp2_common/hardware_ticks/ticks.c.o" "CMakeFiles/tcpServer.dir/home/embedded/pico/pico-sdk/src/rp2_common/hardware_xosc/xosc.c.o" "CMakeFiles/tcpServer.dir/home/embedded/pico/pico-sdk/lib/lwip/src/core/init.c.o" "CMakeFiles/tcpServer.dir/home/embedded/pico/pico-sdk/lib/lwip/src/core/def.c.o" "CMakeFiles/tcpServer.dir/home/embedded/pico/pico-sdk/lib/lwip/src/core/dns.c.o" "CMakeFiles/tcpServer.dir/home/embedded/pico/pico-sdk/lib/lwip/src/core/inet_chksum.c.o" "CMakeFiles/tcpServer.dir/home/embedded/pico/pico-sdk/lib/lwip/src/core/ip.c.o" "CMakeFiles/tcpServer.dir/home/embedded/pico/pico-sdk/lib/lwip/src/core/mem.c.o" "CMakeFiles/tcpServer.dir/home/embedded/pico/pico-sdk/lib/lwip/src/core/memp.c.o" "CMakeFiles/tcpServer.dir/home/embedded/pico/pico-sdk/lib/lwip/src/core/netif.c.o" "CMakeFiles/tcpServer.dir/home/embedded/pico/pico-sdk/lib/lwip/src/core/pbuf.c.o" "CMakeFiles/tcpServer.dir/home/embedded/pico/pico-sdk/lib/lwip/src/core/raw.c.o" "CMakeFiles/tcpServer.dir/home/embedded/pico/pico-sdk/lib/lwip/src/core/stats.c.o" "CMakeFiles/tcpServer.dir/home/embedded/pico/pico-sdk/lib/lwip/src/core/sys.c.o" "CMakeFiles/tcpServer.dir/home/embedded/pico/pico-sdk/lib/lwip/src/core/altcp.c.o" "CMakeFiles/tcpServer.dir/home/embedded/pico/pico-sdk/lib/lwip/src/core/altcp_alloc.c.o" "CMakeFiles/tcpServer.dir/home/embedded/pico/pico-sdk/lib/lwip/src/core/altcp_tcp.c.o" "CMakeFiles/tcpServer.dir/home/embedded/pico/pico-sdk/lib/lwip/src/core/tcp.c.o" "CMakeFiles/tcpServer.dir/home/embedded/pico/pico-sdk/lib/lwip/src/core/tcp_in.c.o" "CMakeFiles/tcpServer.dir/home/embedded/pico/pico-sdk/lib/lwip/src/core/tcp_out.c.o" "CMakeFiles/tcpServer.dir/home/embedded/pico/pico-sdk/lib/lwip/src/core/timeouts.c.o" "CMakeFiles/tcpServer.dir/home/embedded/pico/pico-sdk/lib/lwip/src/core/udp.c.o" "CMakeFiles/tcpServer.dir/home/embedded/pico/pico-sdk/lib/lwip/src/core/ipv4/autoip.c.o" "CMakeFiles/tcpServer.dir/home/embedded/pico/pico-sdk/lib/lwip/src/core/ipv4/dhcp.c.o" "CMakeFiles/tcpServer.dir/home/embedded/pico/pico-sdk/lib/lwip/src/core/ipv4/etharp.c.o" "CMakeFiles/tcpServer.dir/home/embedded/pico/pico-sdk/lib/lwip/src/core/ipv4/icmp.c.o" "CMakeFiles/tcpServer.dir/home/embedded/pico/pico-sdk/lib/lwip/src/core/ipv4/igmp.c.o" "CMakeFiles/tcpServer.dir/home/embedded/pico/pico-sdk/lib/lwip/src/core/ipv4/ip4_frag.c.o" "CMakeFiles/tcpServer.dir/home/embedded/pico/pico-sdk/lib/lwip/src/core/ipv4/ip4.c.o" "CMakeFiles/tcpServer.dir/home/embedded/pico/pico-sdk/lib/lwip/src/core/ipv4/ip4_addr.c.o" "CMakeFiles/tcpServer.dir/home/embedded/pico/pico-sdk/lib/lwip/src/core/ipv4/acd.c.o" "CMakeFiles/tcpServer.dir/home/embedded/pico/pico-sdk/lib/lwip/src/core/ipv6/dhcp6.c.o" "CMakeFiles/tcpServer.dir/home/embedded/pico/pico-sdk/lib/lwip/src/core/ipv6/ethip6.c.o" "CMakeFiles/tcpServer.dir/home/embedded/pico/pico-sdk/lib/lwip/src/core/ipv6/icmp6.c.o" "CMakeFiles/tcpServer.dir/home/embedded/pico/pico-sdk/lib/lwip/src/core/ipv6/inet6.c.o" "CMakeFiles/tcpServer.dir/home/embedded/pico/pico-sdk/lib/lwip/src/core/ipv6/ip6.c.o" "CMakeFiles/tcpServer.dir/home/embedded/pico/pico-sdk/lib/lwip/src/core/ipv6/ip6_addr.c.o" "CMakeFiles/tcpServer.dir/home/embedded/pico/pico-sdk/lib/lwip/src/core/ipv6/ip6_frag.c.o" "CMakeFiles/tcpServer.dir/home/embedded/pico/pico-sdk/lib/lwip/src/core/ipv6/mld6.c.o" "CMakeFiles/tcpServer.dir/home/embedded/pico/pico-sdk/lib/lwip/src/core/ipv6/nd6.c.o" "CMakeFiles/tcpServer.dir/home/embedded/pico/pico-sdk/lib/lwip/src/api/api_lib.c.o" "CMakeFiles/tcpServer.dir/home/embedded/pico/pico-sdk/lib/lwip/src/api/api_msg.c.o" "CMakeFiles/tcpServer.dir/home/embedded/pico/pico-sdk/lib/lwip/src/api/err.c.o" "CMakeFiles/tcpServer.dir/home/embedded/pico/pico-sdk/lib/lwip/src/api/if_api.c.o" "CMakeFiles/tcpServer.dir/home/embedded/pico/pico-sdk/lib/lwip/src/api/netbuf.c.o" "CMakeFiles/tcpServer.dir/home/embedded/pico/pico-sdk/lib/lwip/src/api/netdb.c.o" "CMakeFiles/tcpServer.dir/home/embedded/pico/pico-sdk/lib/lwip/src/api/netifapi.c.o" "CMakeFiles/tcpServer.dir/home/embedded/pico/pico-sdk/lib/lwip/src/api/sockets.c.o" "CMakeFiles/tcpServer.dir/home/embedded/pico/pico-sdk/lib/lwip/src/api/tcpip.c.o" "CMakeFiles/tcpServer.dir/home/embedded/pico/pico-sdk/lib/lwip/src/netif/ethernet.c.o" "CMakeFiles/tcpServer.dir/home/embedded/pico/pico-sdk/lib/lwip/src/netif/bridgeif.c.o" "CMakeFiles/tcpServer.dir/home/embedded/pico/pico-sdk/lib/lwip/src/netif/bridgeif_fdb.c.o" "CMakeFiles/tcpServer.dir/home/embedded/pico/pico-sdk/lib/lwip/src/netif/slipif.c.o" "CMakeFiles/tcpServer.dir/home/embedded/pico/pico-sdk/lib/lwip/src/netif/lowpan6_common.c.o" "CMakeFiles/tcpServer.dir/home/embedded/pico/pico-sdk/lib/lwip/src/netif/lowpan6.c.o" "CMakeFiles/tcpServer.dir/home/embedded/pico/pico-sdk/lib/lwip/src/netif/lowpan6_ble.c.o" "CMakeFiles/tcpServer.dir/home/embedded/pico/pico-sdk/lib/lwip/src/netif/zepif.c.o" "CMakeFiles/tcpServer.dir/home/embedded/pico/pico-sdk/lib/lwip/src/netif/ppp/auth.c.o" "CMakeFiles/tcpServer.dir/home/embedded/pico/pico-sdk/lib/lwip/src/netif/ppp/ccp.c.o" "CMakeFiles/tcpServer.dir/home/embedded/pico/pico-sdk/lib/lwip/src/netif/ppp/chap-md5.c.o" "CMakeFiles/tcpServer.dir/home/embedded/pico/pico-sdk/lib/lwip/src/netif/ppp/chap_ms.c.o" "CMakeFiles/tcpServer.dir/home/embedded/pico/pico-sdk/lib/lwip/src/netif/ppp/chap-new.c.o" "CMakeFiles/tcpServer.dir/home/embedded/pico/pico-sdk/lib/lwip/src/netif/ppp/demand.c.o" "CMakeFiles/tcpServer.dir/home/embedded/pico/pico-sdk/lib/lwip/src/netif/ppp/eap.c.o" "CMakeFiles/tcpServer.dir/home/embedded/pico/pico-sdk/lib/lwip/src/netif/ppp/ecp.c.o" "CMakeFiles/tcpServer.dir/home/embedded/pico/pico-sdk/lib/lwip/src/netif/ppp/eui64.c.o" "CMakeFiles/tcpServer.dir/home/embedded/pico/pico-sdk/lib/lwip/src/netif/ppp/fsm.c.o" "CMakeFiles/tcpServer.dir/home/embedded/pico/pico-sdk/lib/lwip/src/netif/ppp/ipcp.c.o" "CMakeFiles/tcpServer.dir/home/embedded/pico/pico-sdk/lib/lwip/src/netif/ppp/ipv6cp.c.o" "CMakeFiles/tcpServer.dir/home/embedded/pico/pico-sdk/lib/lwip/src/netif/ppp/lcp.c.o" "CMakeFiles/tcpServer.dir/home/embedded/pico/pico-sdk/lib/lwip/src/netif/ppp/magic.c.o" "CMakeFiles/tcpServer.dir/home/embedded/pico/pico-sdk/lib/lwip/src/netif/ppp/mppe.c.o" "CMakeFiles/tcpServer.dir/home/embedded/pico/pico-sdk/lib/lwip/src/netif/ppp/multilink.c.o" "CMakeFiles/tcpServer.dir/home/embedded/pico/pico-sdk/lib/lwip/src/netif/ppp/ppp.c.o" "CMakeFiles/tcpServer.dir/home/embedded/pico/pico-sdk/lib/lwip/src/netif/ppp/pppapi.c.o" "CMakeFiles/tcpServer.dir/home/embedded/pico/pico-sdk/lib/lwip/src/netif/ppp/pppcrypt.c.o" "CMakeFiles/tcpServer.dir/home/embedded/pico/pico-sdk/lib/lwip/src/netif/ppp/pppoe.c.o" "CMakeFiles/tcpServer.dir/home/embedded/pico/pico-sdk/lib/lwip/src/netif/ppp/pppol2tp.c.o" "CMakeFiles/tcpServer.dir/home/embedded/pico/pico-sdk/lib/lwip/src/netif/ppp/pppos.c.o" "CMakeFiles/tcpServer.dir/home/embedded/pico/pico-sdk/lib/lwip/src/netif/ppp/upap.c.o" "CMakeFiles/tcpServer.dir/home/embedded/pico/pico-sdk/lib/lwip/src/netif/ppp/utils.c.o" "CMakeFiles/tcpServer.dir/home/embedded/pico/pico-sdk/lib/lwip/src/netif/ppp/vj.c.o" "CMakeFiles/tcpServer.dir/home/embedded/pico/pico-sdk/lib/lwip/src/netif/ppp/polarssl/arc4.c.o" "CMakeFiles/tcpServer.dir/home/embedded/pico/pico-sdk/lib/lwip/src/netif/ppp/polarssl/des.c.o" "CMakeFiles/tcpServer.dir/home/embedded/pico/pico-sdk/lib/lwip/src/netif/ppp/polarssl/md4.c.o" "CMakeFiles/tcpServer.dir/home/embedded/pico/pico-sdk/lib/lwip/src/netif/ppp/polarssl/md5.c.o" "CMakeFiles/tcpServer.dir/home/embedded/pico/pico-sdk/lib/lwip/src/netif/ppp/polarssl/sha1.c.o" "CMakeFiles/tcpServer.dir/home/embedded/pico/pico-sdk/src/rp2_common/pico_cyw43_arch/cyw43_arch.c.o" "CMakeFiles/tcpServer.dir/home/embedded/pico/pico-sdk/src/rp2_common/pico_cyw43_arch/cyw43_arch_poll.c.o" "CMakeFiles/tcpServer.dir/home/embedded/pico/pico-sdk/src/rp2_common/pico_cyw43_arch/cyw43_arch_threadsafe_background.c.o" "CMakeFiles/tcpServer.dir/home/embedded/pico/pico-sdk/src/rp2_common/pico_cyw43_arch/cyw43_arch_freertos.c.o" "CMakeFiles/tcpServer.dir/home/embedded/pico/pico-sdk/src/rp2_common/pico_cyw43_driver/cyw43_bus_pio_spi.c.o" "CMakeFiles/tcpServer.dir/home/embedded/pico/pico-sdk/lib/cyw43-driver/src/cyw43_ll.c.o" "CMakeFiles/tcpServer.dir/home/embedded/pico/pico-sdk/lib/cyw43-driver/src/cyw43_stats.c.o" "CMakeFiles/tcpServer.dir/home/embedded/pico/pico-sdk/lib/cyw43-driver/src/cyw43_lwip.c.o" "CMakeFiles/tcpServer.dir/home/embedded/pico/pico-sdk/lib/cyw43-driver/src/cyw43_ctrl.c.o" "CMakeFiles/tcpServer.dir/home/embedded/pico/pico-sdk/src/rp2_common/pico_cyw43_driver/cybt_shared_bus/cybt_shared_bus.c.o" "CMakeFiles/tcpServer.dir/home/embedded/pico/pico-sdk/src/rp2_common/pico_cyw43_driver/cybt_shared_bus/cybt_shared_bus_driver.c.o" "CMakeFiles/tcpServer.dir/home/embedded/pico/pico-sdk/src/rp2_common/hardware_pio/pio.c.o" "CMakeFiles/tcpServer.dir/home/embedded/pico/pico-sdk/src/rp2_common/hardware_dma/dma.c.o" "CMakeFiles/tcpServer.dir/home/embedded/pico/pico-sdk/src/rp2_common/hardware_exception/exception.c.o" "CMakeFiles/tcpServer.dir/home/embedded/pico/pico-sdk/src/rp2_common/pico_cyw43_driver/cyw43_driver.c.o" "CMakeFiles/tcpServer.dir/home/embedded/pico/pico-sdk/src/rp2_common/pico_async_context/async_context_threadsafe_background.c.o" "CMakeFiles/tcpServer.dir/home/embedded/pico/pico-sdk/src/rp2_common/pico_stdlib/stdlib.c.o" "CMakeFiles/tcpServer.dir/home/embedded/pico/pico-sdk/src/rp2_common/hardware_uart/uart.c.o" "CMakeFiles/tcpServer.dir/home/embedded/pico/pico-sdk/src/rp2_common/hardware_divider/divider.S.o" "CMakeFiles/tcpServer.dir/home/embedded/pico/pico-sdk/src/rp2_common/pico_runtime/runtime.c.o" "CMakeFiles/tcpServer.dir/home/embedded/pico/pico-sdk/src/rp2_common/pico_runtime_init/runtime_init.c.o" "CMakeFiles/tcpServer.dir/home/embedded/pico/pico-sdk/src/rp2_common/pico_runtime_init/runtime_init_clocks.c.o" "CMakeFiles/tcpServer.dir/home/embedded/pico/pico-sdk/src/rp2_common/pico_runtime_init/runtime_init_stack_guard.c.o" "CMakeFiles/tcpServer.dir/home/embedded/pico/pico-sdk/src/rp2_common/pico_bit_ops/bit_ops_aeabi.S.o" "CMakeFiles/tcpServer.dir/home/embedded/pico/pico-sdk/src/rp2_common/pico_divider/divider_hardware.S.o" "CMakeFiles/tcpServer.dir/home/embedded/pico/pico-sdk/src/rp2_common/pico_double/double_aeabi_rp2040.S.o" "CMakeFiles/tcpServer.dir/home/embedded/pico/pico-sdk/src/rp2_common/pico_double/double_init_rom_rp2040.c.o" "CMakeFiles/tcpServer.dir/home/embedded/pico/pico-sdk/src/rp2_common/pico_double/double_math.c.o" "CMakeFiles/tcpServer.dir/home/embedded/pico/pico-sdk/src/rp2_common/pico_double/double_v1_rom_shim_rp2040.S.o" "CMakeFiles/tcpServer.dir/home/embedded/pico/pico-sdk/src/rp2_common/pico_int64_ops/pico_int64_ops_aeabi.S.o" "CMakeFiles/tcpServer.dir/home/embedded/pico/pico-sdk/src/rp2_common/pico_float/float_aeabi_rp2040.S.o" "CMakeFiles/tcpServer.dir/home/embedded/pico/pico-sdk/src/rp2_common/pico_float/float_init_rom_rp2040.c.o" "CMakeFiles/tcpServer.dir/home/embedded/pico/pico-sdk/src/rp2_common/pico_float/float_math.c.o" "CMakeFiles/tcpServer.dir/home/embedded/pico/pico-sdk/src/rp2_common/pico_float/float_v1_rom_shim_rp2040.S.o" "CMakeFiles/tcpServer.dir/home/embedded/pico/pico-sdk/src/rp2_common/pico_malloc/malloc.c.o" "CMakeFiles/tcpServer.dir/home/embedded/pico/pico-sdk/src/rp2_common/pico_mem_ops/mem_ops_aeabi.S.o" "CMakeFiles/tcpServer.dir/home/embedded/pico/pico-sdk/src/rp2_common/pico_atomic/atomic.c.o" "CMakeFiles/tcpServer.dir/home/embedded/pico/pico-sdk/src/rp2_common/pico_cxx_options/new_delete.cpp.o" "CMakeFiles/tcpServer.dir/home/embedded/pico/pico-sdk/src/rp2_common/pico_standard_binary_info/standard_binary_info.c.o" "CMakeFiles/tcpServer.dir/home/embedded/pico/pico-sdk/src/rp2_common/pico_printf/printf.c.o" "CMakeFiles/tcpServer.dir/home/embedded/pico/pico-sdk/src/rp2_common/pico_crt0/crt0.S.o" "CMakeFiles/tcpServer.dir/home/embedded/pico/pico-sdk/src/rp2_common/pico_clib_interface/newlib_interface.c.o" "CMakeFiles/tcpServer.dir/home/embedded/pico/pico-sdk/src/rp2_common/pico_stdio/stdio.c.o" "CMakeFiles/tcpServer.dir/home/embedded/pico/pico-sdk/src/rp2_common/pico_stdio_usb/reset_interface.c.o" "CMakeFiles/tcpServer.dir/home/embedded/pico/pico-sdk/src/rp2_common/pico_stdio_usb/stdio_usb.c.o" "CMakeFiles/tcpServer.dir/home/embedded/pico/pico-sdk/src/rp2_common/pico_stdio_usb/stdio_usb_descriptors.c.o" "CMakeFiles/tcpServer.dir/home/embedded/pico/pico-sdk/lib/tinyusb/src/portable/raspberrypi/rp2040/dcd_rp2040.c.o" "CMakeFiles/tcpServer.dir/home/embedded/pico/pico-sdk/lib/tinyusb/src/portable/raspberrypi/rp2040/rp2040_usb.c.o" "CMakeFiles/tcpServer.dir/home/embedded/pico/pico-sdk/lib/tinyusb/src/device/usbd.c.o" "CMakeFiles/tcpServer.dir/home/embedded/pico/pico-sdk/lib/tinyusb/src/device/usbd_control.c.o" "CMakeFiles/tcpServer.dir/home/embedded/pico/pico-sdk/lib/tinyusb/src/class/audio/audio_device.c.o" "CMakeFiles/tcpServer.dir/home/embedded/pico/pico-sdk/lib/tinyusb/src/class/cdc/cdc_device.c.o" "CMakeFiles/tcpServer.dir/home/embedded/pico/pico-sdk/lib/tinyusb/src/class/dfu/dfu_device.c.o" "CMakeFiles/tcpServer.dir/home/embedded/pico/pico-sdk/lib/tinyusb/src/class/dfu/dfu_rt_device.c.o" "CMakeFiles/tcpServer.dir/home/embedded/pico/pico-sdk/lib/tinyusb/src/class/hid/hid_device.c.o" "CMakeFiles/tcpServer.dir/home/embedded/pico/pico-sdk/lib/tinyusb/src/class/midi/midi_device.c.o" "CMakeFiles/tcpServer.dir/home/embedded/pico/pico-sdk/lib/tinyusb/src/class/msc/msc_device.c.o" "CMakeFiles/tcpServer.dir/home/embedded/pico/pico-sdk/lib/tinyusb/src/class/net/ecm_rndis_device.c.o" "CMakeFiles/tcpServer.dir/home/embedded/pico/pico-sdk/lib/tinyusb/src/class/net/ncm_device.c.o" "CMakeFiles/tcpServer.dir/home/embedded/pico/pico-sdk/lib/tinyusb/src/class/usbtmc/usbtmc_device.c.o" "CMakeFiles/tcpServer.dir/home/embedded/pico/pico-sdk/lib/tinyusb/src/class/vendor/vendor_device.c.o" "CMakeFiles/tcpServer.dir/home/embedded/pico/pico-sdk/lib/tinyusb/src/class/video/video_device.c.o" "CMakeFiles/tcpServer.dir/home/embedded/pico/pico-sdk/lib/tinyusb/src/tusb.c.o" "CMakeFiles/tcpServer.dir/home/embedded/pico/pico-sdk/lib/tinyusb/src/common/tusb_fifo.c.o" "CMakeFiles/tcpServer.dir/home/embedded/pico/pico-sdk/src/rp2_common/pico_fix/rp2040_usb_device_enumeration/rp2040_usb_device_enumeration.c.o" "CMakeFiles/tcpServer.dir/home/embedded/pico/pico-sdk/src/rp2_common/hardware_adc/adc.c.o" -o tcpServer.elf  pico-sdk/src/rp2040/boot_stage2/CMakeFiles/bs2_default_library.dir/bs2_default_padded_checksummed.S.o

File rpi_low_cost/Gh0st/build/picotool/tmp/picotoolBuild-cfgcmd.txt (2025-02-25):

cmd='/usr/bin/cmake;--no-warn-unused-cli;-DCMAKE_MAKE_PROGRAM:FILEPATH=/usr/bin/gmake;-DPICO_SDK_PATH:FILEPATH=/home/embedded/pico/pico-sdk;-DPICOTOOL_NO_LIBUSB=1;-DPICOTOOL_FLAT_INSTALL=1;-DCMAKE_INSTALL_PREFIX=/home/embedded/pico/Gh0st/build/_deps;-DCMAKE_RULE_MESSAGES=OFF;-DCMAKE_INSTALL_MESSAGE=NEVER;-GUnix Makefiles;-S;<SOURCE_DIR><SOURCE_SUBDIR>;-B;<BINARY_DIR>'

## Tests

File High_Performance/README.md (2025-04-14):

# High-Performance Microcontroller Board

## Overview:
The High-Performance Microcontroller Board integrates a 24-bit ADC to capture high-resolution EEG signals and transmits the data wirelessly using an ESP32-based development board. 
The setup allows seamless data transfer to an ESP32-C6 module, which then relays the EEG data over WiFi (ESPNOW) to a connected laptop for analysis and visualization.


Figure:EEG dataset pipeline from data collection to visualization

## System workflow:
1. EEG signals are captured from snap electrodes and processed using an ESP32 development board.
2. The ESP32 development board transmits the 8-channel EEG data wirelessly via ESPNOW to the ESP32-C6 module.
3. The ESP32-C6 receives the data and relays it to the Arduino Serial Monitor for verification.
4. A Python script captures the data from the laptop's serial port and records it in a text file. 
5. The data is formatted for compatibility with the OpenBCI GUI for visualization and further analysis.
6. Additionally, another python script records the labeled data in csv file for evaluation using the machine learning pipeline.
7. Filtering techniques are applied to extract alpha wave frequencies (8-10 Hz), confirming the presence of neural activity.
8. Initial testing involved verifying ADC readings with a DC voltage input, ensuring data accuracy before integrating electrodes.
   data collection stages

## Data transmission and performance
1. The system initially transmitted data at **1 sample per second** to establish a stable connection.
2. Once stable, the sampling rate was increased to **250 samples per second**.
3. ESPNOW protocol was used to establish a reliable WiFi link between the ESP32 devices.
4. The hardware was validated by successfully detecting alpha waves, demonstrating its efficiency in EEG signal acquisition.

## Key features of the High-Performance Microcontroller Board
1. **Optimized PCB design**: The board features a **four-layer PCB**, minimizing ground and supply plane resistance to reduce noise.
2. **High-resolution ADC**: The **ADS1299** offers a **96 dB PSRR at 60 Hz**, ensuring minimal interference and high precision.
3. **Battery-powered operation**: Runs on a **low-resistance rechargeable battery**, reducing power noise and increasing reliability.
4. **Integrated pre-amplifiers**: The ADS1299 has built-in **programmable gain amplifiers**, reducing external component requirements and failure risks.
5. **Dual polarity power supply**: Converts single-polarity battery voltage into **dual polarity supply**, allowing the ADC to handle positive and negative inputs.
6. **Power-efficient ESP32 processor**: Equipped with **dual 32-bit RISC cores**, consuming an average of **78.32 mW** in active mode.
7. **Wireless connectivity**: Supports **Bluetooth & WiFi**, with ESPNOW ensuring **250 samples/sec continuous operation**.
8. **Rechargeable & portable**: Features a **USB-rechargeable battery**, on/off and reset switches, and a lightweight design for improved user experience.
9. **Expandable channel support**: The system supports an additional **ADS1299 module**, increasing EEG channels from **8 to 16**.

## Files
1. **document_data.py**: This Python script is responsible for capturing and processing the EEG data received from the ESP32-C6 over the serial port (formatted for viewing using OpenBCI GUI).
2. **Firmware/ReceiverCode/ReceiverCode.ino**: This Arduino sketch runs on the ESP32-C6, which acts as the receiver of the EEG data transmitted via WiFi (ESPNOW).
3. **Firmware/SenderCode/SenderCode.h**: Header file containing function prototypes and constants used by SenderCode.cpp and SenderCode.ino.
4. **Firmware/SenderCode/SenderCode.cpp**: This file implements core functions for acquiring EEG signals and transmitting them via ESPNOW.
5. **Firmware/SenderCode/SenderCode.ino**: The main Arduino sketch for the ESP32 (EEG signal acquisition & transmission).
6. **Recorded_Data/eeg_data_to_file.py:** The python script for collecting and labelling blinking EEG data (formatted for easy processing using machine learning pipeline).
7. **CAD/high_performance_board_protective_case.stl** The 3D model of a custom-designed protective case meant to safeguard a high-performance board from physical damage, environmental factors, and overheating.

## **Installation & Setup**

### **1. Downloads**
- **Arduino IDE**
- **ESP32 Board Package** (via Arduino Board Manager)
- **Python (3.8+)**
- **PySerial Library** (`pip install pyserial`)
- **OpenBCI GUI**
- **pynput Library** (`pip install pynput`)

### **2. Hardware Requirements**
- **ESP32 Dev Board with ESP32-S3-WROOM-1 and 24-bit ADC** [https://www.aliexpress.us/item/3256806073268159.html?spm=a2g0o.order_list.order_list_main.20.54681802966XjN&gatewayAdapt=glo2usa](https://www.aliexpress.us/item/3256806073268159.html?spm=a2g0o.order_list.order_list_main.20.54681802966XjN&gatewayAdapt=glo2usa)
- **ESP32-C6**  
- **EEG Headset** 
- **2 USB Cables** (USB-C)

## **Setup and execution**
### **1. Setting Up the ESP32 & ESP32-C6**
- Install Arduino IDE and ESP32 board package.
- Upload **SenderCode.ino** to the ESP32 high-performance board.
- Upload **ReceiverCode.ino** to the ESP32-C6 module.

### **2. Running the Python Script**
For visualization:
- `pip install pyserial`
- `python3 document_data.py`
For data labelling:
- `pip install pynput`
- `python3 eeg_data_to_file.py`

## Usage Instructions
1. **Hardware setup**
   A- Connect EEG snap electrodes to the ADS1299 board.
   B- Ensure the ESP32 development board and ESP32-C6 module are powered and configured.
   C- Ensure that all the electrodes are in contact with the scalp.


Figure:EEG Headset and high performance board (encased in custom case)

3. **Data acquisition**
   A- Open the Arduino Serial Monitor to check real-time EEG data transmission.
   B- Run the provided Python script to capture data from the serial port.
reciever

Figure:Receiver code run on XIAO-ESP32-C6 board to obtain 8-channel data via WiFi visible in the serial monitor
python_script

Figure:Python script writing the data  to a text file

5. **Visualization and analysis**
   A- View the recorded data in OpenBCI GUI to visualze the EEG data for all 8 channels.
GUI
   
Figure:EEG 8 channel data in the GUI Interface


Figure:EEG 8 channel data recorded in csv file

## Protective case design overview


## References
1. [https://www.ti.com/product/ADS1299](https://www.ti.com/product/ADS1299)
2. [https://docs.openbci.com/](https://docs.openbci.com/)
3. [https://datasheet.octopart.com/ADS1299IPAG-Texas-Instrumentsdatasheet-17020782.pdf](https://datasheet.octopart.com/ADS1299IPAG-Texas-Instruments-datasheet-17020782.pdf)
4. [https://openbci.com/community/concentratetoday-neurofeedback-enhancing-concentration-level/](https://openbci.com/community/concentratetoday-neurofeedback-enhancing-concentration-level/)

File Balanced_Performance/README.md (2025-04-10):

# Balanced Performance Board

## Overview
The Balanced Performance Board bridges commercial products and DIY EEG boards by featuring high resolution ADC chip, ADS1299, on a DIY PCB, a common microcontroller, and a custom made GUI. 

The specifications include:
|  Section |  Feature  | Specs |
| --- | --- | --- |
| ADS1299 Breakout Board**      | Dimensions              | 56.10mm x 69.00mm         |
|                  | Layers                  | 2-layer PCB                            |
|                  | Electrode Connector     | Straight header pins/connectors        |
| Balanced Backpack Board**      | Dimensions              | 35.56mm x 77.47mm        |
|                  | Layers                  | 2-layer PCB                            |
|                  | Electrode Connector     | 2.54mm right-angle JST                 |
| Microcontroller  | Model                   | DFRobot Firebeetle ESP32 32D           |
|                  | Processor               | Tensilica LX6 dual core                |
|                  | Clock Speed             | <240MHz                                |
|                  | Flash / RAM             | 16MB Flash / 520KB RAM                 |
| ADC              | AFE Chip                | ADS1299                                |
|                  | Number of Channels      | 8 (16 with Daisy Chaining)             |
|                  | ADC Resolution          | 24-bit                                 |
|                  | Input Impedance         | >1 GΩ                                  |
|                  | Gain                    | Programmable up to 24x                 |
|                  | Sampling Rate           | 16kHz - 250Hz per channel              |
| Power            | Supply Voltage          | USB (Supply 3.3V and 5V)               |
| Connectivity     | Interfaces              | USB, Bluetooth (BLE)                   |
|                  | Data Rate               | <1Mbps                                 |

** There are two designs of the Balanced Performance board. The ADS1299 Breakout board is a flat board that has header pins for each input/output for the ADS1299. This board is more meticulous to wire but it provides an easy way to interface with the ADS1299 depending on the project. The Balanced Backpack board acts as a backpack on top of the DFRobot ESP32 microcontroller which makes it compact and easier to connect. It only provides the electrode outputs, everything else is connected to the microcontroller. 

## PCB Designs

|  ADS1299 Breakout Board  |  Balanced Backpack Board  |
| --- | --- |
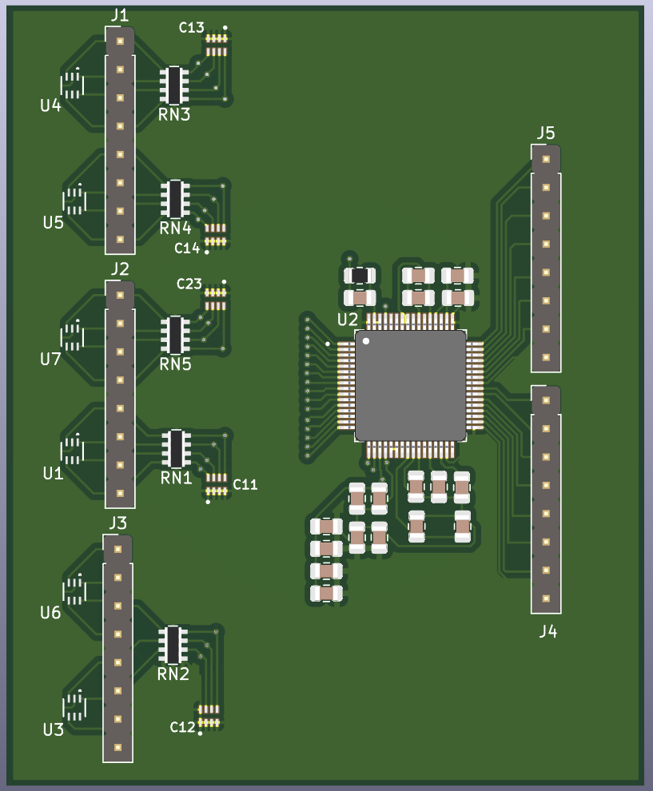
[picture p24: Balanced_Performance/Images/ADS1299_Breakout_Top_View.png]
|  |  |

## Setup Instructions
### 1. Wiring
The connections listed should be universal when using the ADS1299. Refer to your PCB schematic for specific leads and/or ADS1299 Datasheet. In our case, the ADS1299 Breakout Board had these direct connections:

| ADS1299 Breakout Board      | Firebeetle ESP32 | Description    |
| --------          | -------          | -------        |
| SCLK              | SCLK [GPIO 18]   | Set to 1.5MHz[^1]**    |
| MISO [DOUT]       | MISO [GPIO 19]   | Data channel output (ADS1299 → ESP32)[^1]  |
| MOSI [DIN]        | MOSI [GPIO 23]   | Data channel input (ESP32 → ADS1299)[^1]   |
| CS or SS          | SS [GPIO 5]      | Chip select (low during communication)[^1] |
| DRDY              | GPIO 4           | Data ready (low when new data available)[^1] |
| RST               | GPIO 2           | Reset (active low)[^2]     |
| START             | GPIO 10          | START (active high)[^3]     |
| AVDD**            | 5V [VCC]         | Analog Nominal 5V[^4]      |
| AVSS**            | GND              | Analog Referenced to GND   |
| DVDD              | 3.3V             | Digital Nominal 1.8V[^4]   |
| AGND and DGND     | GND              | Tied ground                |

** The SCLK can vary in speed. Most documentation online uses 2MHz or 4MHz, but we found when using these values, we had inconsistencies with the data reading or data corruption. 1.5MHz is the minimum spec for the external clock in the ADS1299 and works best for our system. 
** The ADS1299 can be powered using unipolar power supplies (5V on AVDD and referenced to GND on VSS) and with bipolar supplies (2.5V on AVDD and -2.5V on AVSS).

For the Balanced Backpack Board, since it sits directly ontop of the microcontroller there is no need to wire anything. Only unsure the orientation is correct with the headers (the curved end of the pcb goes towards the power end of the microcontroller)

[^1]: https://www.ti.com/lit/ds/symlink/ads1299.pdf#page=38
[^2]: https://www.ti.com/lit/ds/symlink/ads1299.pdf#page=35
[^3]: https://www.ti.com/lit/ds/symlink/ads1299.pdf#page=34
[^4]: https://www.ti.com/lit/ds/symlink/ads1299.pdf#page=8

### 2. Clone the Repository
If not already done so, clone the respository

```bash
git clone https://github.com/Keith-Khadar/Gh05t
```

## 3. Upload the Sketch
Copy the esp32\ADS1299 library and place it under your libraries directory of your Arduino IDE. You can usually find this under  ```"C:\Users\"USER"\Documents\Arduino\libraries"```. By adding the library, you can reference to it when flashing the sketch.
 - ***SKETCH***: Depending on the microcontroller that is used, the user may need to change the sketch to configure it to their device. The only line that needs to be changed is ```ADS.initialize(16,2,13,1.5,0);``` This line controls the pinout for the DRDY, RST, and CS. 

 - ***ADS12999 LIBRARY***: The library folder was retrieved from OpenBCI[^5] which used the ADS1299 library that was created by Conor Russomanno[^6] initially. The only changes that we made were for ESP32 adapation instead of the Arduino Uno.
   - Adaption includes:
     - Changing the SPI interface to fit ESP32 instead of Arduino Uno. This is changing how it is setup and how data is sent/received.
     - The only line that will need to change according to the users setup is ```SPI.begin(18, 19, 23, CS); SPI.beginTransaction(SPISettings(Freq * 1000000, MSBFIRST, SPI_MODE1));``` 
    These lines control the SPI clock and pinouts for the DOUT and DIN. If a different esp32 is being used, the pinouts with be different (refer to wiring table for our pinout setup).

[^5]: https://github.com/chipaudette/OpenBCI
[^6]: https://github.com/conorrussomanno/ADS1299

Flash the ```esp32\esp32_ble_eeg\ADS1299_SPI_ESP.ino``` program to the ESP32 microcontroller using either Arduino IDE or PlatformIO. Ensure the output of the ESP32 reports the BLE server broadcasting.

### 4. Confirm Connections and Broadcasting
In order to confirm proper connections with the PCB, there is debugging points in the sketch. Open the Serial Monitor and connect to 115200 baud rate in order to read the outputs of the device. 

The device should output the ID of the ADS1299 that is being used. In our case the ID register should output 0x3E (0b00111110)[^7]. If it outputs 0x00 there is something wrong with the wiring or the ADS1299 is not being supplied enough power (most likely the analog (AVDD or AVSS)).
  - We encountered an issue where we were able to read from the registers but was not able to read from the channels properly. Make sure to triple check wiring and the analog power is being supplied properly with minimal noise. 

[^7]: https://www.ti.com/lit/ds/symlink/ads1299.pdf#page=45

In order to confirm the BLE broadcast, you can check any device that has bluetooth support and see if the device name "ADS1299 BLE" is shown in the list. 

### 5. Update Configuration
Edit the `ble_handler.py` file, under utils folder, to update the ESP32 service and characteristic UUID:

```python
SERVICE_UUID = "XXXXXXXX-XXXX-XXXX-XXXX-XXXXXXXXXXXX"  # Replace with ESP32 Service UUID
CHARACTERISTIC_UUID = "XXXXXXXX-XXXX-XXXX-XXXX-XXXXXXXXXXXX" # Replace with ESP32 Characteristic UUID
```

There are UUID already defined in the code, but if you like to keep unique devices, we recommend to change the UUID.

### 6. Connect to the GUI
Refer to the GUI section for setup.

## Troubleshooting/Known Bugs
- None

## Future Work
- Expanding the documentation to support more microcontrollers.

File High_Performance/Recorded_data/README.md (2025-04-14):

# EEG data collection and labelling

## Overview
This project captures the 8 channel EEG data, processes the received hex values into decimal format, and logs them into a CSV file. The script also allows live labeling of data based on whether the user’s eyes are open or closed, using simple keyboard input ('c' for closed, 'o' for open).

## Features
- Reads data from an ESP32 via a serial connection.
- Converts hexadecimal EEG readings into decimal values.
- Logs data with a timestamp in a CSV file.
- Allows real-time labeling using the keyboard:
'c' → Mark as "eyes closed"
'o' → Mark as "eyes open"
- Keyboard listener runs in a background thread while collecting data.

## Installation
### Prerequisites
Ensure you have Python installed on your system.

### Required Python Packages
Install the required dependencies using pip:
```sh
pip install pyserial
```

## Hardware Setup
1. Connect the ESP32 + ADS1299 development board to your computer via a USB-C cable.
2. Ensure the correct serial port (`COM4` in this case) is selected in the script.

## Usage
1. Run the script:
   ```sh
   python3 eeg_data_to_file.py
   ```
2. The script will automatically start listening for incoming serial data.
3. Press the `c` key to indicate that your eyes are closed and press `o` key to indicate that your eyes are open.
4. Press `Ctrl+C` to stop the script.

## File Output
The script creates a CSV file (`received_data.csv`) with the following columns:
- Sample index
- EEG data from 8 electrodes (Fp1, Fp2, C3, C4, P7, P8, O1, O2)
- Timestamp
- Eyes closed (1 if `Tab` is pressed, 0 otherwise)



Figure: Sample CSV file

## Note
- The data files can be fed into the machine learning pipeline for gathering valuable insights from blinking data.
- Logging data to a file is a time-intensive process, which may introduce delays in recording all incoming data. As a result, capturing all samples per second may not always be achievable.

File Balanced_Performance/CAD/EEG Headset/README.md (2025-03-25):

# 3D-Printed EEG Headset

## Overview
This folder hosts 3D printable files for assembling the EEG headset designed to securely hold electrodes in place for capturing brainwave signals. 
The design ensures proper electrode placement while maintaining comfort and stability during use.

## Files
1) hexagonal_fitting.stl – Secures the electrodes in place with a tight fit.
2) medium_headset_front_half.stl – Front section of the EEG headset frame.
3) medium_headset_back_half.stl – Back section of the EEG headset frame.
4) wire_clip.stl – Manages and organizes electrode wires.
5) electrode_holder.stl – Electrode holder component ensuring stable contact with the scalp.
6) fastening_screw.stl – Fastening component for structural stability.

## Printing Instructions
Software- UltiMaker Cura
Material- PLA (Polylactic Acid)
Print settings-
* Infill density: 15%
* Support overhang angle: 60.0

* Build plate adhesion: Brim (for halves of the headset) or Skirt (for all other components)

## Materials
EEG Headset Frame (2 halves)
Spring fittings (x 10)
Snap-buttons (x 12) 
Electrode holders (x 10)
Fastening screws (x 10)
Copper wire of 12cm (x 12)
Electrodes (x 10)
Wires (x 12)
Wire clips (x 16)
Sandpaper for post-processing
Wire clipper for removing the excess support prints especially from the EEG headset halves

## Assembly Instructions
1) Print all above components.

2) Ensure that any excess printed support structures have been remove from the headset halves, and that all rough edges are sanded smooth for comfort. 
   Test the fit of the halves before proceeding to ensure they align properly and then glue them together.
3) Glue the hexagonal fitting into the designated slots on the inside of the headset at appropriate positions according to the 10-20 system (FP1, FP2, C3, C4, P7, P8, 01, 02).
4) Take the spring fittings and screw them into the fastening screws. These springs once positioned securely, will provide the adjustable fit for the headset.
5) Now, push the wider side of the electrode holder in the fastening screw against the spring from the inner side of the headset.
6) Glue the snap buttons to the electrode holder with the finer end protruding outward and the flat end soldered to a mulit-strand copper wire.

7) Each copper wire is in turn soldered to one end of the jumper wire, the other end is attached to the headers on the board.
8) Attach wire clip to minimize tangling of the wires.


## Usage Guidelines
Adjust the headset for a snug but comfortable fit.
Regularly check the integrity of the solder connections and adjust the electrode placement using the fitting screw as needed for consistent performance.

## Future work
The design of the electrode and board covers is being worked upon.

## Credit
This design is inspired by and builds upon the open-source EEG headset designs from OpenBCI, [https://github.com/OpenBCI/Ultracortex/tree/master/Mark_IV](https://github.com/OpenBCI/Ultracortex/tree/master/Mark_IV). \
Their contributions to the neurotechnology community are invaluable.

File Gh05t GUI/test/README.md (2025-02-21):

# Unit Tests for the GUI

## Overview
This repository contains unit tests for the GH05T GUI. These tests check the functionality of the interface and ensure a bug free user experience.

## Running the Tests
To run the unit tests (make sure to be in the parent directory of the GUI):
run ```python -m unittest discover test```

## Unit Tests Overview

1. **test_initial_state**
   - **Purpose:** Tests the initial state of the main window.
   - **Checks:** Window title, visibility of widgets, and status bar message.

2. **test_file_input_action**
   - **Purpose:** Tests the action of inputting a file.
   - **Checks:** Visibility of the row2 widget and updates to the status bar upon file selection.

3. **test_initial_widget_visibility**
   - **Purpose:** Tests the visibility of widgets upon startup.
   - **Checks:** Visibility of the data input button and other buttons (play, export, add plot).

4. **test_load_data_widget_visibility**
   - **Purpose:** Tests the visibility of widgets after loading data.
   - **Checks:** Ensures buttons are visible after a file is selected.

5. **test_play_data_stream**
   - **Purpose:** Tests the functionality of the play data stream button.
   - **Checks:** Button text, play animation state, and status bar message when no plots are available.

6. **test_export_data_to_file**
   - **Purpose:** Tests the functionality to export data to a file.
   - **Checks:** Status bar message confirming successful export after selecting a file.

7. **test_add_plot**
   - **Purpose:** Tests adding a new plot to the main window.
   - **Checks:** Number of plots and status bar message after adding a time series plot.

8. **test_add_multiple_plots**
   - **Purpose:** Tests adding multiple plots to the main window.
   - **Checks:** Total number of plots and status bar message after adding an FFT plot.

9. **test_load_play_data_stream**
   - **Purpose:** Tests the functionality of the play data stream button with plots loaded.
   - **Checks:** Button text, play animation state, and status bar message indicating playback status.

10. **test_real_time_input_action_failure**
    - **Purpose:** Tests the behavior of the real-time input action in case of a failure (device not found).
    - **Checks:** Visibility of the row2 widget and status bar message indicating connection issues.

11. **test_close_application**
    - **Purpose:** Tests that the application closes properly.
    - **Checks:** Ensures that the main window is no longer visible after closing.

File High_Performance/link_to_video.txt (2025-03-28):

https://uflorida-my.sharepoint.com/:v:/g/personal/stuti_ruparel_ufl_edu/EWC_1qLaFP9MvUYRoi2DBm8B5WgjMIX73doYVd1gvHtIrA?e=2BOrGF&nav=eyJyZWZlcnJhbEluZm8iOnsicmVmZXJyYWxBcHAiOiJTdHJlYW1XZWJBcHAiLCJyZWZlcnJhbFZpZXciOiJTaGFyZURpYWxvZy1MaW5rIiwicmVmZXJyYWxBcHBQbGF0Zm9ybSI6IldlYiIsInJlZmVycmFsTW9kZSI6InZpZXcifX0%3D

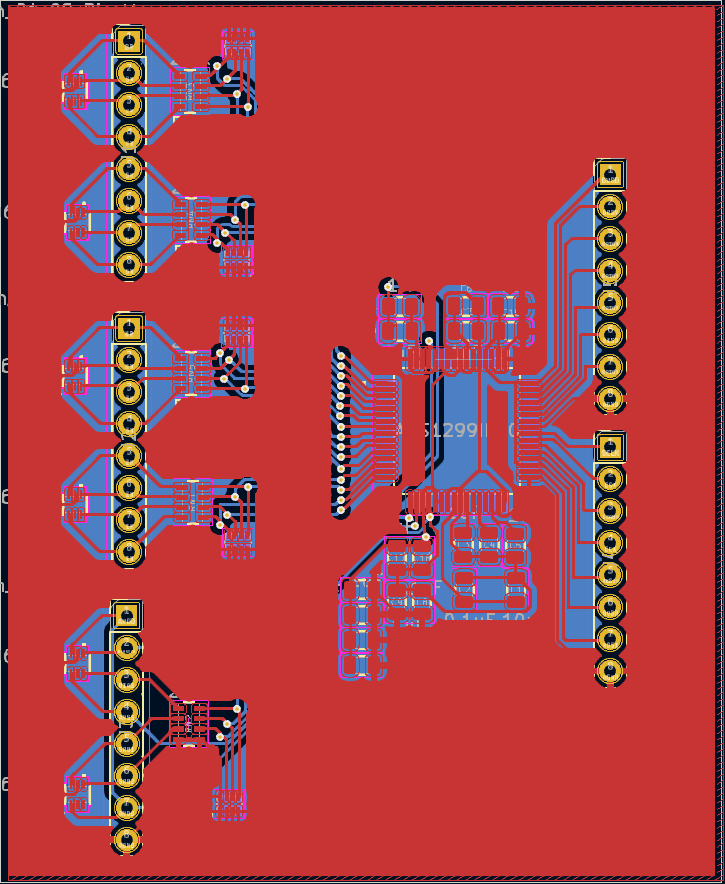
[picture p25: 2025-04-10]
Balanced_Performance/Images/ADS1299_Breakout_Board.png

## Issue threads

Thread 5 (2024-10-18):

### ISSUE TITLE
Instrumentation Amplifier

### ISSUE THREAD

**Issue by Keith-Khadar** [Keith-Khadar/Gh05t#5]
Look into the circuit needed to amplify the signal from the electrodes into a useable form.

**Comment by piprtay** [comment]
There are some projects that use this as their signal amplifier : https://docs.rs-online.com/6d2f/A700000006877304.pdf
The lowest price I found was $55. We can look at this for reference since this also combines a instrumentation amplifer, 4 channel op amp ic, reference voltage ic, and some other components.

**Comment by Keith-Khadar** [comment]
Here is an article on how to make a portable eeg, they also describe the circuit they used for their instrumentation amplifier 
Luan B, Sun M, Jia W. Portable Amplifier Design for a Novel EEG Monitor in Point-of-Care Applications. Proc IEEE Annu Northeast Bioeng Conf. 2012;2012:388-389. doi: 10.1109/nebc.2012.6207127. PMID: 25339843; PMCID: PMC4203429.

**Comment by Keith-Khadar** [comment]
https://www.bitbrain.com/blog/eeg-amplifier

This talks about all the specs we need for the amplifier

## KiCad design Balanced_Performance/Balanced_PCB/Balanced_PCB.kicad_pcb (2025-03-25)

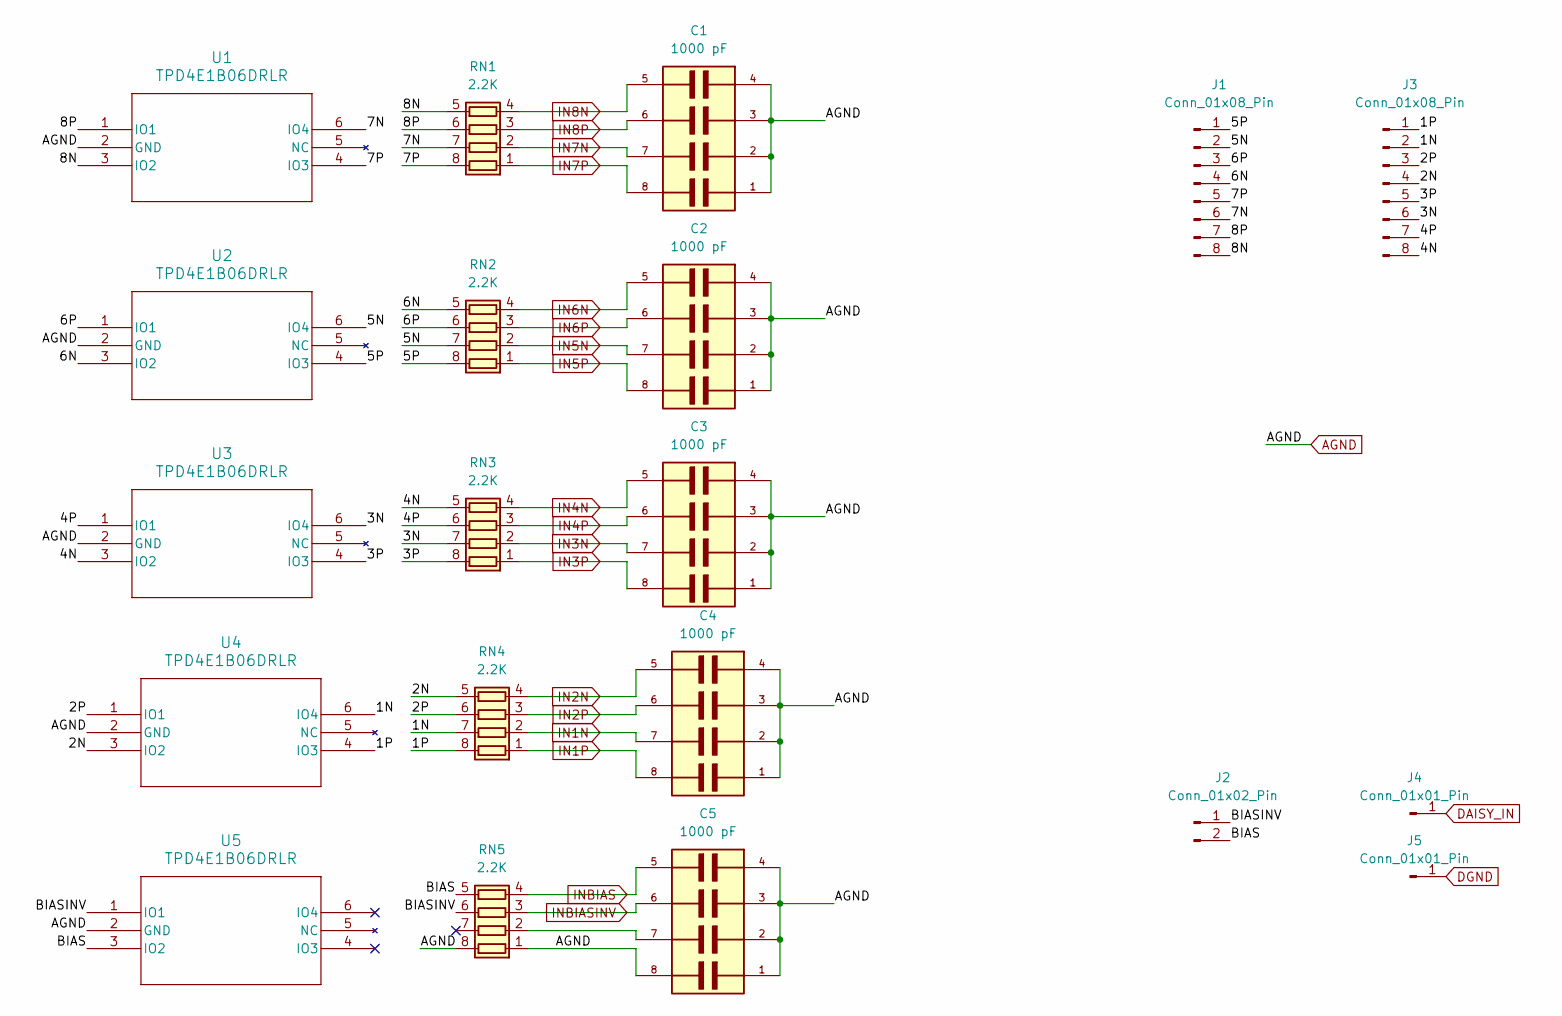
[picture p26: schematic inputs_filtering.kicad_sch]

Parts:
C1, C2, C3, C4, C5: 1000 pF; CAPCAV_W3A45C102KAT2A-8; PARTREV Dec 2014
J1, J3: Conn_01x08_Pin; JST_XH_S8B-XH-A_1x08_P2.50mm_Horizontal
J2: Conn_01x02_Pin; JST_XH_S2B-XH-A_1x02_P2.50mm_Horizontal
J4, J5: Conn_01x01_Pin; TestPoint_Pad_D2.5mm
RN1, RN2, RN3, RN4, RN5: 2.2K; R_Array_Concave_4x0603
U1, U2, U3, U4, U5: TPD4E1B06DRLR; DRL6_TEX

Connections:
/Inputs & Filtering/1N: J3.2, RN4.7 (R2.2), U4.6 (IO4)
/Inputs & Filtering/1P: J3.1, RN4.8 (R1.2), U4.4 (IO3)
/Inputs & Filtering/2N: J3.4, RN4.5 (R4.2), U4.3 (IO2)
/Inputs & Filtering/2P: J3.3, RN4.6 (R3.2), U4.1 (IO1)
/Inputs & Filtering/3N: J3.6, RN3.7 (R2.2), U3.6 (IO4)
/Inputs & Filtering/3P: J3.5, RN3.8 (R1.2), U3.4 (IO3)
/Inputs & Filtering/4N: J3.8, RN3.5 (R4.2), U3.3 (IO2)
/Inputs & Filtering/4P: J3.7, RN3.6 (R3.2), U3.1 (IO1)
/Inputs & Filtering/5N: J1.2, RN2.7 (R2.2), U2.6 (IO4)
/Inputs & Filtering/5P: J1.1, RN2.8 (R1.2), U2.4 (IO3)
/Inputs & Filtering/6N: J1.4, RN2.5 (R4.2), U2.3 (IO2)
/Inputs & Filtering/6P: J1.3, RN2.6 (R3.2), U2.1 (IO1)
/Inputs & Filtering/7N: J1.6, RN1.7 (R2.2), U1.6 (IO4)
/Inputs & Filtering/7P: J1.5, RN1.8 (R1.2), U1.4 (IO3)
/Inputs & Filtering/8N: J1.8, RN1.5 (R4.2), U1.3 (IO2)
/Inputs & Filtering/8P: J1.7, RN1.6 (R3.2), U1.1 (IO1)
/Inputs & Filtering/BIAS: J2.2, RN5.5 (R4.2), U5.3 (IO2)
/Inputs & Filtering/BIASINV: J2.1, RN5.6 (R3.2), U5.1 (IO1)
AGND: C1.1, C1.2, C1.3, C1.4, C2.1, C2.2, C2.3, C2.4, C3.1, C3.2, C3.3, C3.4, C4.1, C4.2, C4.3, C4.4, C5.1, C5.2, C5.3, C5.4, C5.8, J5.1, RN5.1 (R1.1), RN5.8 (R1.2), U1.2 (GND), U2.2 (GND), U3.2 (GND), U4.2 (GND), U5.2 (GND); also elsewhere on the board
DAISY_IN: J4.1; also elsewhere on the board
IN1N: C4.7, RN4.2 (R2.1); also elsewhere on the board
IN1P: C4.8, RN4.1 (R1.1); also elsewhere on the board
IN2N: C4.5, RN4.4 (R4.1); also elsewhere on the board
IN2P: C4.6, RN4.3 (R3.1); also elsewhere on the board
IN3N: C3.7, RN3.2 (R2.1); also elsewhere on the board
IN3P: C3.8, RN3.1 (R1.1); also elsewhere on the board
IN4N: C3.5, RN3.4 (R4.1); also elsewhere on the board
IN4P: C3.6, RN3.3 (R3.1); also elsewhere on the board
IN5N: C2.7, RN2.2 (R2.1); also elsewhere on the board
IN5P: C2.8, RN2.1 (R1.1); also elsewhere on the board
IN6N: C2.5, RN2.4 (R4.1); also elsewhere on the board
IN6P: C2.6, RN2.3 (R3.1); also elsewhere on the board
IN7N: C1.7, RN1.2 (R2.1); also elsewhere on the board
IN7P: C1.8, RN1.1 (R1.1); also elsewhere on the board
IN8N: C1.5, RN1.4 (R4.1); also elsewhere on the board
IN8P: C1.6, RN1.3 (R3.1); also elsewhere on the board
INBIAS: C5.5, RN5.4 (R4.1); also elsewhere on the board
INBIASINV: C5.6, RN5.3 (R3.1); also elsewhere on the board
unnamed: C5.7, RN5.2 (R2.1)

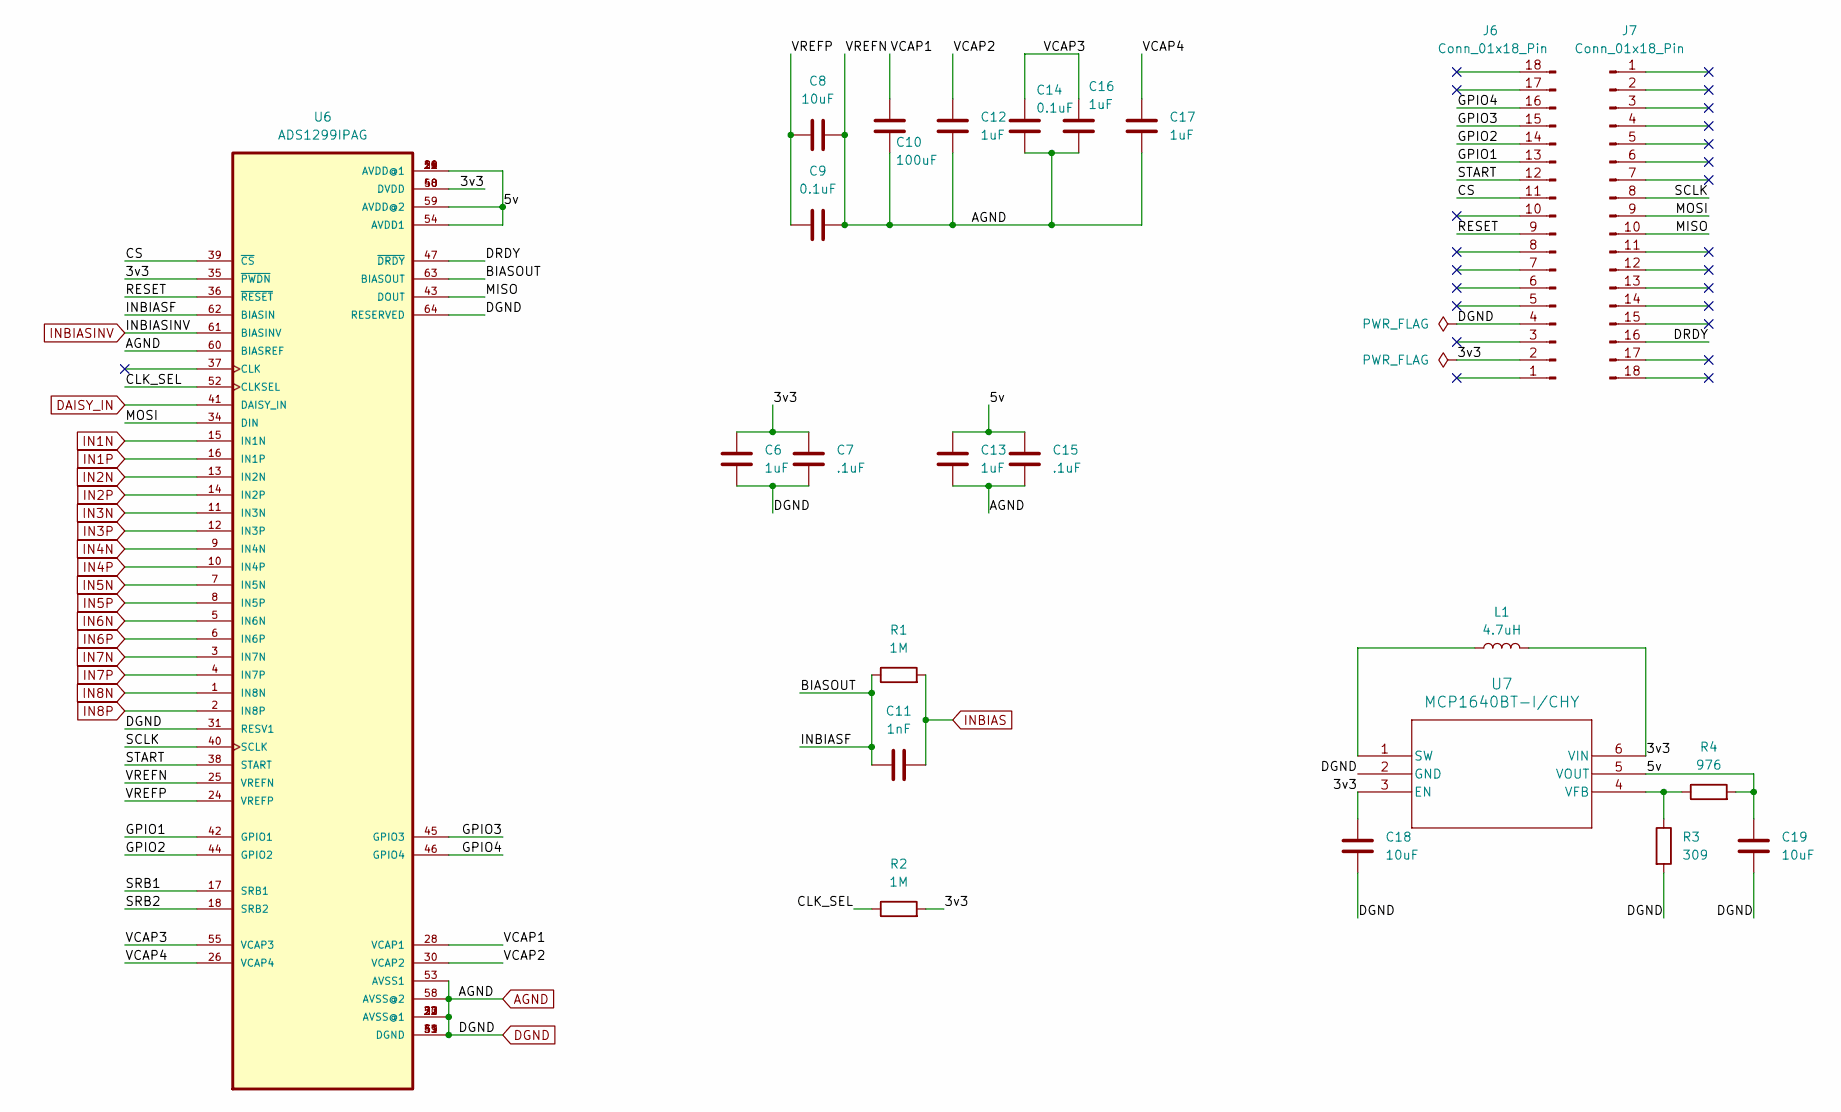
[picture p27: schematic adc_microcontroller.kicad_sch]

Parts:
C6, C12, C13, C16, C17: 1uF; C_0805_2012Metric
C7, C15: .1uF; C_0805_2012Metric
C8, C18, C19: 10uF; C_0805_2012Metric
C9, C14: 0.1uF; C_0805_2012Metric
C10: 100uF; C_0805_2012Metric
C11: 1nF; C_0805_2012Metric
J6, J7: Conn_01x18_Pin; PinSocket_1x18_P2.54mm_Vertical
L1: 4.7uH; L_0805_2012Metric
R1, R2: 1M; R_0805_2012Metric
R3: 309; R_0805_2012Metric
R4: 976; R_0805_2012Metric
U6: ADS1299IPAG; QFP50P1200X1200X120-64N
U7: MCP1640BT-I/CHY; SOT-23-6_MC_MCH

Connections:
/ADS1299 & Microcontroller/3v3: C6.1, C7.1, C18.2, J6.2, L1.2, R2.2, U6.35 (~PWDN), U6.48 (DVDD), U6.50 (DVDD), U7.3 (EN), U7.6 (VIN)
/ADS1299 & Microcontroller/5v: C13.1, C15.1, C19.1, R4.2, U6.19 (AVDD@1), U6.21 (AVDD@1), U6.22 (AVDD@1), U6.54 (AVDD1), U6.56 (AVDD@1), U6.59 (AVDD@2), U7.5 (VOUT)
/ADS1299 & Microcontroller/BIASOUT: C11.2, R1.1, U6.62 (BIASIN), U6.63 (BIASOUT)
/ADS1299 & Microcontroller/CLK_SEL: R2.1, U6.52 (CLKSEL)
/ADS1299 & Microcontroller/CS: J6.11, U6.39 (~CS)
/ADS1299 & Microcontroller/DRDY: J7.16, U6.47 (~DRDY)
/ADS1299 & Microcontroller/GPIO1: J6.13, U6.42 (GPIO1)
/ADS1299 & Microcontroller/GPIO2: J6.14, U6.44 (GPIO2)
/ADS1299 & Microcontroller/GPIO3: J6.15, U6.45 (GPIO3)
/ADS1299 & Microcontroller/GPIO4: J6.16, U6.46 (GPIO4)
/ADS1299 & Microcontroller/MISO: J7.10, U6.43 (DOUT)
/ADS1299 & Microcontroller/MOSI: J7.9, U6.34 (DIN)
/ADS1299 & Microcontroller/RESET: J6.9, U6.36 (~RESET)
/ADS1299 & Microcontroller/SCLK: J7.8, U6.40 (SCLK)
/ADS1299 & Microcontroller/SRB1: U6.17 (SRB1)
/ADS1299 & Microcontroller/SRB2: U6.18 (SRB2)
/ADS1299 & Microcontroller/START: J6.12, U6.38 (START)
/ADS1299 & Microcontroller/VCAP1: C10.1, U6.28 (VCAP1)
/ADS1299 & Microcontroller/VCAP2: C12.1, U6.30 (VCAP2)
/ADS1299 & Microcontroller/VCAP3: C14.2, C16.1, U6.55 (VCAP3)
/ADS1299 & Microcontroller/VCAP4: C17.1, U6.26 (VCAP4)
/ADS1299 & Microcontroller/VREFP: C8.1, C9.1, U6.24 (VREFP)
AGND: C6.2, C7.2, C8.2, C9.2, C10.2, C12.2, C13.2, C14.1, C15.2, C16.2, C17.2, C18.1, C19.2, J6.4, R3.2, U6.20 (AVSS@1), U6.23 (AVSS@1), U6.25 (VREFN), U6.31 (RESV1), U6.32 (AVSS@1), U6.33 (DGND), U6.49 (DGND), U6.51 (DGND), U6.53 (AVSS1), U6.57 (AVSS@1), U6.58 (AVSS@2), U6.60 (BIASREF), U6.64 (RESERVED), U7.2 (GND); also elsewhere on the board
DAISY_IN: U6.41 (DAISY_IN); also elsewhere on the board
IN1N: U6.15 (IN1N); also elsewhere on the board
IN1P: U6.16 (IN1P); also elsewhere on the board
IN2N: U6.13 (IN2N); also elsewhere on the board
IN2P: U6.14 (IN2P); also elsewhere on the board
IN3N: U6.11 (IN3N); also elsewhere on the board
IN3P: U6.12 (IN3P); also elsewhere on the board
IN4N: U6.9 (IN4N); also elsewhere on the board
IN4P: U6.10 (IN4P); also elsewhere on the board
IN5N: U6.7 (IN5N); also elsewhere on the board
IN5P: U6.8 (IN5P); also elsewhere on the board
IN6N: U6.5 (IN6N); also elsewhere on the board
IN6P: U6.6 (IN6P); also elsewhere on the board
IN7N: U6.3 (IN7N); also elsewhere on the board
IN7P: U6.4 (IN7P); also elsewhere on the board
IN8N: U6.1 (IN8N); also elsewhere on the board
IN8P: U6.2 (IN8P); also elsewhere on the board
INBIAS: C11.1, R1.2; also elsewhere on the board
INBIASINV: U6.61 (BIASINV); also elsewhere on the board
unnamed: L1.1, U7.1 (SW)
unnamed: R3.1, R4.1, U7.4 (VFB)

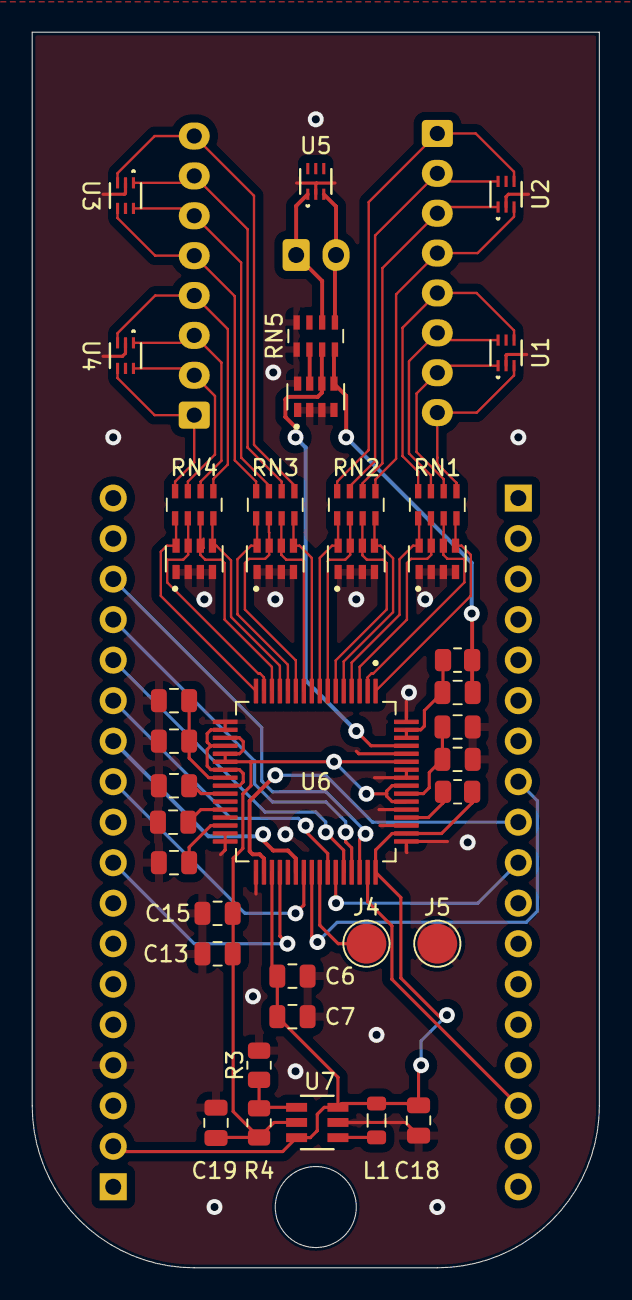
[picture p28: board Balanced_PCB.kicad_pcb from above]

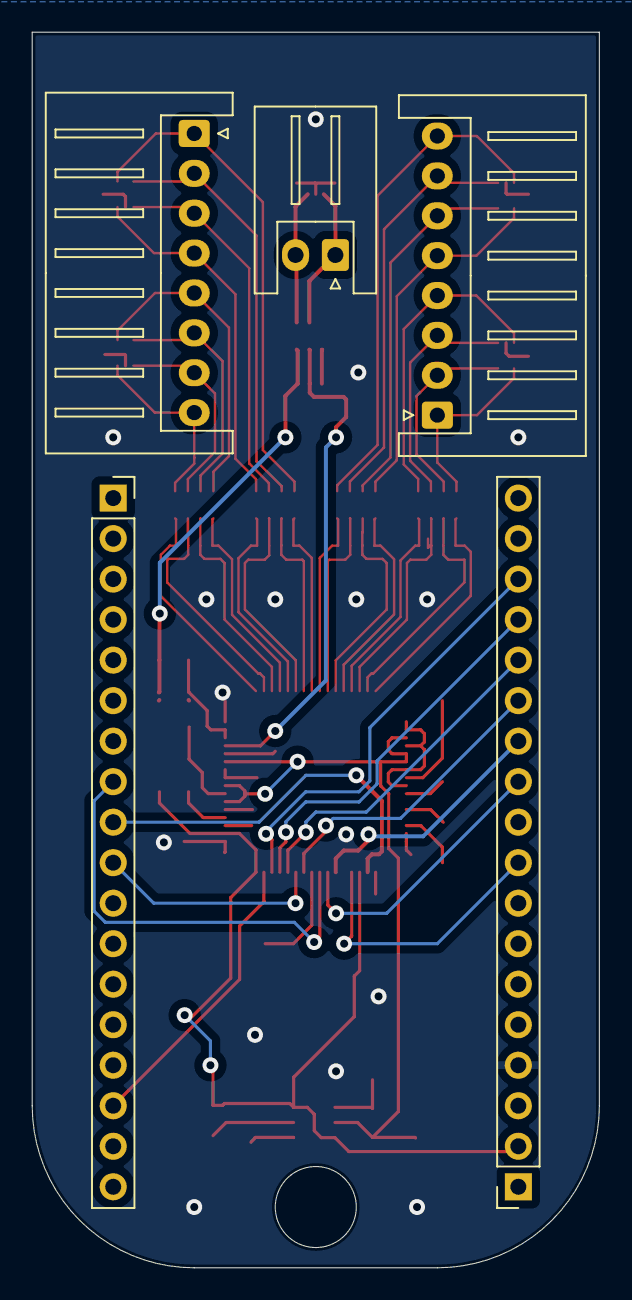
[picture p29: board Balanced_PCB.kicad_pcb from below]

Board: 4 copper layers, 35.6 x 77.5 mm, 43 parts (5 on the bottom side), 61 nets.

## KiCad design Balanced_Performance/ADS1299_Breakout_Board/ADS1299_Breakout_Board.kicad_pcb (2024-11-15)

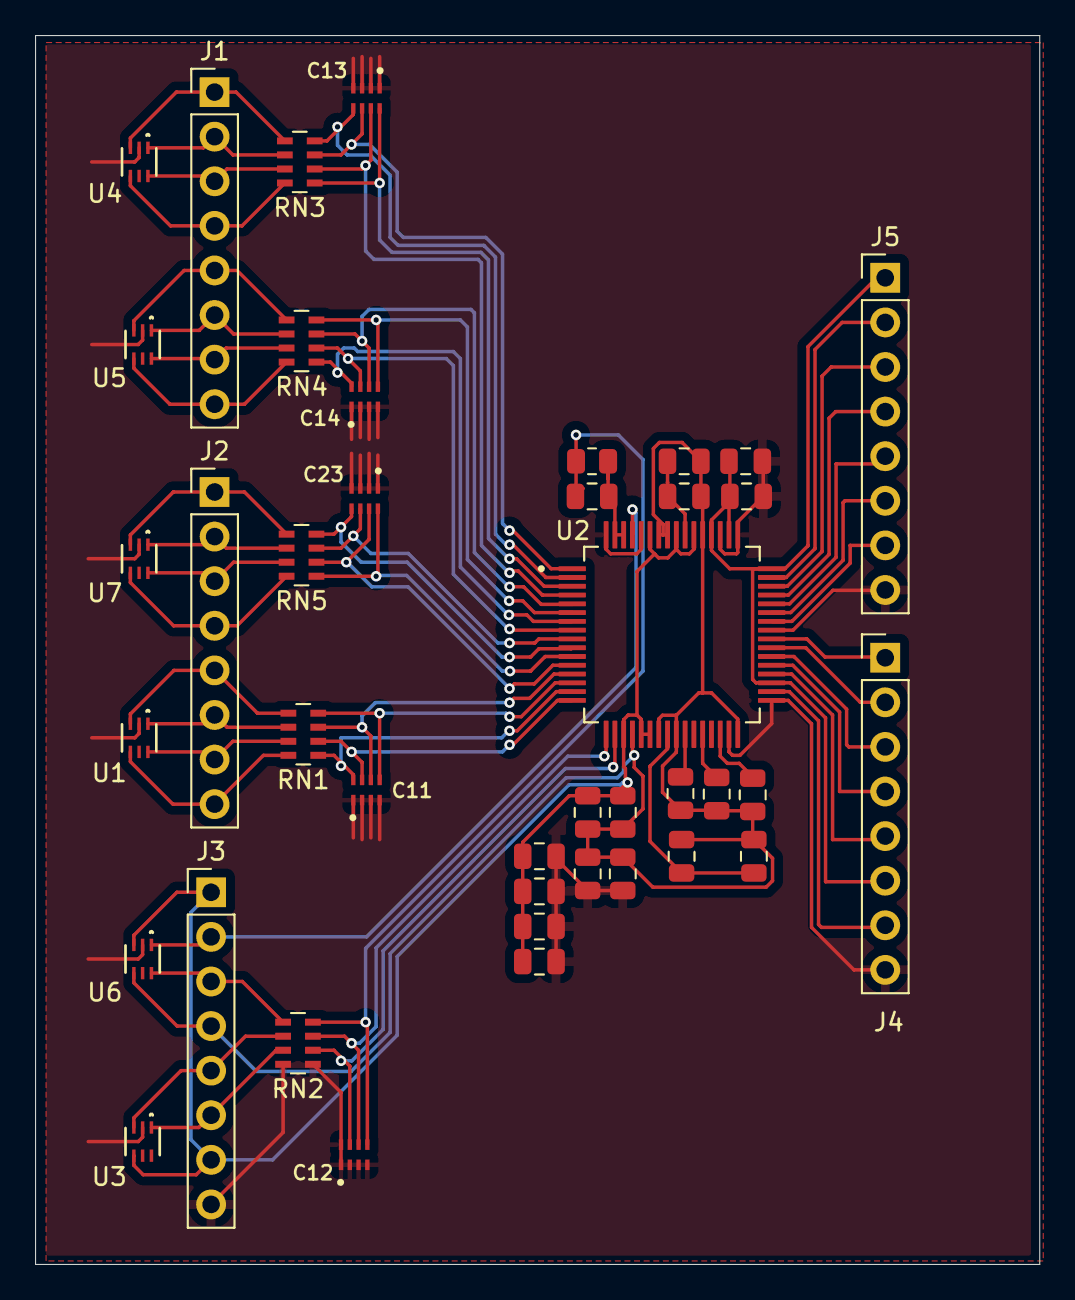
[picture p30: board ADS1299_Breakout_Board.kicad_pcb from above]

Board: 2 copper layers, 57.2 x 70.0 mm, 41 parts (0 on the bottom side), 61 nets.

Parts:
C1: 10uF; C_0805_2012Metric
C2, C6: 0.1uF; C_0805_2012Metric
C3, C5, C7, C8, C9, C15, C17, C19, C21: 1uF; C_0805_2012Metric
C4: 100uF; C_0805_2012Metric
C10: 1nF; C_0805_2012Metric
C11, C12, C13, C14, C23: 1000 pF; CAPCAF50P200X125X85-8
C16, C18, C20, C22: .1uF; C_0805_2012Metric
J1, J2, J3, J4, J5: Conn_01x08_Pin; PinHeader_1x08_P2.54mm_Vertical
R1: 1M; R_0805_2012Metric
RN1, RN2, RN3, RN4, RN5: 2.2K; R_Array_Concave_4x0603
U1, U3, U4, U5, U6, U7: TPD4E1B06DRLR; DRL6_TEX
U2: ADS1299IPAG; QFP50P1200X1200X120-64N

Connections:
/1N: J2.8, RN1.8 (R1.2), U1.4 (IO3)
/1P: J2.7, RN1.7 (R2.2), U1.6 (IO4)
/2N: J2.6, RN1.6 (R3.2), U1.1 (IO1)
/2P: J2.5, RN1.5 (R4.2), U1.3 (IO2)
/3N: J2.4, RN5.8 (R1.2), U7.4 (IO3)
/3P: J2.3, RN5.7 (R2.2), U7.6 (IO4)
/4N: J2.2, RN5.6 (R3.2), U7.1 (IO1)
/4P: J2.1, RN5.5 (R4.2), U7.3 (IO2)
/5N: J1.8, RN4.8 (R1.2), U5.4 (IO3)
/5P: J1.7, RN4.7 (R2.2), U5.6 (IO4)
/6N: J1.6, RN4.6 (R3.2), U5.1 (IO1)
/6P: J1.5, RN4.5 (R4.2), U5.3 (IO2)
/7N: J1.4, RN3.8 (R1.2), U4.4 (IO3)
/7P: J1.3, RN3.7 (R2.2), U4.6 (IO4)
/8N: J1.2, RN3.6 (R3.2), U4.1 (IO1)
/8P: J1.1, RN3.5 (R4.2), U4.3 (IO2)
/AVDD: C17.1, C18.1, C19.1, C20.1, C21.1, C22.1, J3.1, J3.7, U2.19 (AVDD@1), U2.21 (AVDD@1), U2.22 (AVDD@1), U2.54 (AVDD1), U2.56 (AVDD@1), U2.59 (AVDD@2), U3.4 (IO3), U6.3 (IO2)
/AVSS: C1.2, C2.2, C3.2, C4.2, C5.2, C6.1, C7.2, C8.1, C9.1, C17.2, C18.2, J3.4, U2.20 (AVSS@1), U2.23 (AVSS@1), U2.25 (VREFN), U2.32 (AVSS@1), U2.53 (AVSS1), U2.57 (AVSS@1), U2.58 (AVSS@2), U6.4 (IO3)
/BIAS: J3.3, RN2.5 (R4.2), U6.6 (IO4)
/BIASIN: C10.2, R1.1, U2.62 (BIASIN), U2.63 (BIASOUT)
/BIASINV: J3.2, U2.61 (BIASINV), U6.1 (IO1)
/BIAS_DRV: C10.1, C12.5, R1.2, RN2.4 (R4.1)
/CLK: J4.4, U2.37 (CLK)
/CS1: J4.2, U2.39 (~CS)
/DRDY: J5.2, U2.47 (~DRDY)
/DVDD: C15.1, C16.1, J4.6, J5.1, U2.35 (~PWDN), U2.48 (DVDD), U2.50 (DVDD), U2.52 (CLKSEL)
/GPIO1: J5.7, U2.42 (GPIO1)
/GPIO2: J5.5, U2.44 (GPIO2)
/GPIO3: J5.4, U2.45 (GPIO3)
/GPIO4: J5.3, U2.46 (GPIO4)
/IN1N: C11.8, RN1.1 (R1.1), U2.15 (IN1N)
/IN1P: C11.7, RN1.2 (R2.1), U2.16 (IN1P)
/IN2N: C11.6, RN1.3 (R3.1), U2.13 (IN2N)
/IN2P: C11.5, RN1.4 (R4.1), U2.14 (IN2P)
/IN3N: C23.8, RN5.1 (R1.1), U2.11 (IN3N)
/IN3P: C23.7, RN5.2 (R2.1), U2.12 (IN3P)
/IN4N: C23.6, RN5.3 (R3.1), U2.9 (IN4N)
/IN4P: C23.5, RN5.4 (R4.1), U2.10 (IN4P)
/IN5N: C14.8, RN4.1 (R1.1), U2.7 (IN5N)
/IN5P: C14.7, RN4.2 (R2.1), U2.8 (IN5P)
/IN6N: C14.6, RN4.3 (R3.1), U2.5 (IN6N)
/IN6P: C14.5, RN4.4 (R4.1), U2.6 (IN6P)
/IN7N: C13.8, RN3.1 (R1.1), U2.3 (IN7N)
/IN7P: C13.7, RN3.2 (R2.1), U2.4 (IN7P)
/IN8N: C13.6, RN3.3 (R3.1), U2.1 (IN8N)
/IN8P: C13.5, RN3.4 (R4.1), U2.2 (IN8P)
/MISO: J5.6, U2.43 (DOUT)
/MOSI: J4.7, U2.34 (DIN)
/RESET: J4.5, U2.36 (~RESET)
/SCLK: J4.1, U2.40 (SCLK)
/SRB1: J3.5, RN2.6 (R3.2), U3.3 (IO2)
/SRB2: J3.6, RN2.7 (R2.2), U3.1 (IO1)
/START: J4.3, U2.38 (START)
/VCAP1: C4.1, U2.28 (VCAP1)
/VCAP2: C5.1, U2.30 (VCAP2)
/VCAP3: C6.2, C7.1, U2.55 (VCAP3)
/VCAP4: C3.1, U2.26 (VCAP4)
/VREFP: C1.1, C2.1, U2.24 (VREFP)
/_SRB1: C12.6, RN2.3 (R3.1), U2.17 (SRB1)
/_SRB2: C12.7, RN2.2 (R2.1), U2.18 (SRB2)
AGND: C8.2, C9.2, C11.1, C11.2, C11.3, C11.4, C12.1, C12.2, C12.3, C12.4, C12.8, C13.1, C13.2, C13.3, C13.4, C14.1, C14.2, C14.3, C14.4, C15.2, C16.2, C19.2, C20.2, C21.2, C22.2, C23.1, C23.2, C23.3, C23.4, J3.8, J4.8, J5.8, RN2.1 (R1.1), RN2.8 (R1.2), U1.2 (GND), U2.31 (RESV1), U2.33 (DGND), U2.41 (DAISY_IN), U2.49 (DGND), U2.51 (DGND), U2.60 (BIASREF), U2.64 (RESERVED), U3.2 (GND), U4.2 (GND), U5.2 (GND), U6.2 (GND), U7.2 (GND)

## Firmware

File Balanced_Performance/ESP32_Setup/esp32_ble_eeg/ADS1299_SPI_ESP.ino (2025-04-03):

/* Referenced to https://github.com/chipaudette/OpenBCI Arduino Uno Example and adapted to ESP32
  This example uses the ADS1299 Arduino Library, a software bridge between the ADS1299 chip and 
  Arduino. See http://www.ti.com/product/ads1299 for more information about the device and the README
  folder in the ADS1299 directory for more information about the library.
  
  // ------- FIREBEETLE ESP32 Pin Assignments ------- //
  // SCK = GPIO 18
  // MISO [DOUT] = GPIO 19
  // MOSI [DIN] = GPIO 23
  // CS = GPIO 13 // chip select pin
  // DRDY = GPIO 16 // data ready pin
  // RST = GPIO 2

  // VCC supplies 5V/AVDD while plugged via usb
  // 3.3V supplies DVDD
  // GND to both AGND, AVSS, and DGND

  // ------- XIAO ESP32-C6 Pin Assignments ------- //
  // SCK = GPIO 19 or D8
  // MISO [DOUT] = GPIO 20 or D9
  // MOSI [DIN] = GPIO 18 or D10
  // CS = GPIO 21 or D3 // chip select pin
  // DRDY = GPIO 1 or D1 // data ready pin
  // RST = GPIO 2 or D2

  // VCC supplies 5V/AVDD while plugged via usb
  // 3.3V supplies DVDD
  // GND to both AGND, AVSS, and DGND

    // ------- XIAO ESP32-S3 Pin Assignments ------- //
  // SCK = GPIO 7 or D8
  // MISO [DOUT] = GPIO 8 or D9
  // MOSI [DIN] = GPIO 9 or D10
  // CS = GPIO 44 or D7 // chip select pin
  // DRDY = GPIO 3 or D2 // data ready pin
  // RST = GPIO 2 or D1

  // VCC supplies 5V/AVDD while plugged via usb
  // 3.3V supplies DVDD
  // GND to both AGND, AVSS, and DGND
*/

#include <ADS1299.h>
#include <BLEDevice.h>
#include <BLEServer.h>
#include <BLEUtils.h>
#include <BLE2902.h>

ADS1299 ADS;
BLECharacteristic *pCharacteristic;
BLEServer* pServer = nullptr;
BLEService* pService = nullptr;
bool deviceConnected = false;

#define SERVICE_UUID "4fafc201-1fb5-459e-8fcc-c5c9c331914b" 
#define CHARACTERISTIC_UUID "beb5483e-36e1-4688-b7f5-ea07361b26a8" 
#define CONFIG_ESP_CONSOLE_USB_CDC 0

struct DataPacket {
    unsigned long timestamp;
    int32_t channelData[8];  // Assuming 8 channels
};

class MyServerCallbacks: public BLEServerCallbacks {
    void onConnect(BLEServer* pServer) {
        deviceConnected = true;
        Serial.println("Client connected!");
    };

    void onDisconnect(BLEServer* pServer) {
        deviceConnected = false;
        Serial.println("Client disconnected!");
    }
};

unsigned long startTime;
unsigned long currentTime;

// NMLS Filtering
#define FILTER_ORDER 10
#define MU 0.1f
#define EPS 1e-6f

typedef struct {
    float weights[FILTER_ORDER];
    float buffer[FILTER_ORDER];
    int bufferIndex;
} NLMSFilter;
NLMSFilter nlmsFilters[8];

void initNLMSFilters() {
    for (int ch = 0; ch < 8; ch++) {
        NLMSFilter* filter = &nlmsFilters[ch];
        filter->bufferIndex = 0;
        
        // Initialize weights to zeros (or small random values)
        for (int i = 0; i < FILTER_ORDER; i++) {
            filter->weights[i] = 0.0f;
            filter->buffer[i] = 0.0f;
        }
    }
}

float applyNLMS(NLMSFilter* filter, float noisySample) {
    filter->buffer[filter->bufferIndex] = noisySample;
    
    float y_hat = 0.0f;
    for (int i = 0; i < FILTER_ORDER; i++) {
        int idx = (filter->bufferIndex + i) % FILTER_ORDER;
        y_hat += filter->weights[i] * filter->buffer[idx];
    }
    
    // Compute error
    float e = noisySample - y_hat;
    
    float x_pow = 0.0f;
    for (int i = 0; i < FILTER_ORDER; i++) {
        int idx = (filter->bufferIndex + i) % FILTER_ORDER;
        x_pow += filter->buffer[idx] * filter->buffer[idx];
    }
    
    float mu_eff = MU / (x_pow + EPS);
    
    for (int i = 0; i < FILTER_ORDER; i++) {
        int idx = (filter->bufferIndex + i) % FILTER_ORDER;
        filter->weights[i] += mu_eff * e * filter->buffer[idx];
    }
    
    // Update buffer index
    filter->bufferIndex = (filter->bufferIndex + 1) % FILTER_ORDER;
    
    return e;
}

void setup() {
  // --- FIREBEETLE ESP32 Dev ADS Configurations ---
  // ADS.initialize(16,2,5,2,0);          // (DRDY pin, RST pin, CS pin, SCK frequency in MHz, isDaisy bool);
  ADS.initialize(16, 2, 13, 1.5, 0);      // (DRDY, RST, CS, 1.5MHz)
  // --- ESP32 S3 XIAO SEEED ADS Configurations ---
  // ADS.initialize(3,2,44,2,0);
  
  delay(1000);                            // Give time for USB to stabilize

  Serial.begin(115200);
  Serial.println("ADS1299-ESP32"); 
  delay(1000);

  // Digital Inputs/Outputs Setup for FIREBEETLE
	pinMode(25, INPUT); // GPIO4
  pinMode(26, INPUT); // GPIO3
  pinMode(27, INPUT); // GPIO2
  pinMode(9, INPUT); // GPIO1
  pinMode(10, OUTPUT); // START

  // SETUP DEVICE (Datasheet pg. 62)
  ADS.verbose = true;                     // when verbose is true, there will be Serial feedback 
  ADS.RESET();                            // all registers set to default
  ADS.SDATAC();                           // stop Read Data Continuous mode to communicate with ADS
  ADS.getDeviceID();                      // Confirm register ID                                    
  
  // --- Initialize BLE ---
  BLEDevice::init("ADS1299_BLE");
  BLEDevice::setEncryptionLevel(ESP_BLE_SEC_ENCRYPT);
  BLEDevice::setMTU(517);                 // set max MTU size
  pServer = BLEDevice::createServer();
  pServer->setCallbacks(new MyServerCallbacks());

  pService = pServer->createService(SERVICE_UUID);

  pCharacteristic = pService->createCharacteristic(
      CHARACTERISTIC_UUID,
      BLECharacteristic::PROPERTY_READ |
      BLECharacteristic::PROPERTY_WRITE |
      BLECharacteristic::PROPERTY_NOTIFY
  );
  pCharacteristic->addDescriptor(new BLE2902());
  pService->start();                    // start BLE service

  BLEAdvertising* pAdvertising = BLEDevice::getAdvertising();
  pAdvertising->addServiceUUID(SERVICE_UUID);
  pAdvertising->setScanResponse(true);  // enable scan response for advertising
  pAdvertising->setMinPreferred(0x12);
  pAdvertising->start();
  Serial.println("Waiting for a client connection to notify...");

  // --- SANITY CHECK - Internal Test Signal (Square Wave) ---
  // Config2 Register - Setup test Signal
  // Bit 4 (INT_CAL) = 1 → Enables the internal test signal
  // Bit 2 (CAL_AMP) = 0 or 1 → Choose test signal amplitude
  // Bits 1:0 (CAL_FREQ) = 01 → Selects test signal frequency (fCLK / 2²⁰)
  // ADS.WREG(CONFIG1,0xD6);               // 0b11010110 - 250 SPS
  // ADS.RREG(CONFIG1);                    // verify write
  // ADS.WREG(CONFIG2, 0xD1);              // 0b11010001
  // ADS.RREG(CONFIG2);                    // verify write
  // ADS.WREG(CONFIG3, 0xEC);              // 0b11101100
  // ADS.RREG(CONFIG3);                    // verify write
  // for(byte i=CH1SET; i<=CH8SET; i++){   // set up to modify the 8 channel setting registers
  //   ADS.regData[i] = 0b00000101;        // the regData array mirrors the ADS1299 register addresses
  // }                                  
  // ADS.WREGS(CH1SET,7);                  // write new channel settings
  // ADS.RREGS(CH1SET,7);                  // read out what we just did to verify the write
  
  // --- ELECTRODE READING ---
  ADS.WREG(CONFIG1,0xD6);            // 0b11010110 - 250 SPS
  ADS.RREG(CONFIG1);                 // verify write
  ADS.WREG(CONFIG2,0xC2);            // 0b11000010
  ADS.RREG(CONFIG2);                 // verify write
  ADS.WREG(CONFIG3,0xEC);            // 0b11100100 (external bias) or 0b11101100 (internal bias)
  ADS.RREG(CONFIG3);                 // verify write
  ADS.WREG(MISC1, 0x00);             // closed for SRB1 connection to CHxN - single ended
  // ADS.WREG(MISC1, 0x20);          // closed for SRB1 connection to CHxN - single ended
  ADS.WREG(BIAS_SENSP,0xFF);         // bias derivation for each positive channel
  // ADS.WREG(BIAS_SENSN,0xFF);      // bias derivation for each negative channel

  for(byte i=CH1SET; i<=CH8SET; i++){// set up to modify the 8 channel setting registers
    if (i < CH2SET) {
      ADS.regData[i] = 0x60;         // 0b01100000
    } else {
      ADS.regData[i] = 0xE9;         // 0b11101001 - power down channels
    }
  }
  ADS.WREGS(CH1SET,7);               // write new channel settings
  ADS.RREGS(CH1SET,7); 

  // initNLMSFilters();                 // Apply NLMS Filtering

  digitalWrite(10, HIGH);               // START = 1
  ADS.RDATAC();

  unsigned long startTime = millis();
}

void loop() {
  if (deviceConnected) {
    DataPacket dataPacket;
    unsigned long currentTime = millis();
    dataPacket.timestamp = currentTime-startTime; // capture time in miliseconds
    if (digitalRead(16) == 0) { // DRDY low
      ADS.RDATA(); // Read data from each channel
      float sample = 0.0;

      for (int i = 0; i < 8; i++) {
        // // applying nlms filtering - noise reduction
        // sample = (float)ADS.channelData[i];
        // // // apply NMLS filtering
        // float filteredSample = applyNLMS(&nlmsFilters[i], sample);
        // // // Copy back into channeldata
        // dataPacket.channelData[i] = (int32_t)filteredSample;

        dataPacket.channelData[i] = ADS.channelData[i];
      }

      // Send channel data over BLE
      pCharacteristic->setValue((uint8_t*)&dataPacket, sizeof(DataPacket));
      pCharacteristic->notify();

      Serial.println("===============");
      Serial.print("Timestamp: ");
      Serial.println(dataPacket.timestamp/1000); // convert to seconds
      Serial.print(" Channel Data: ");
      Serial.print(dataPacket.channelData[0]);
      Serial.println();

      // for (int i = 0; i < 8; i++) {
      // int32_t signed24BitData = dataPacket.channelData[i] & 0x00FFFFFF;

      //   // Check if the sign bit (bit 23) is set
      //   if (signed24BitData & 0x00800000) {
      //       // If the sign bit is set, extend the sign to 32 bits
      //       signed24BitData |= 0xFF000000;
      //   }

        // Print the meaningful signed 24-bit data
        // Serial.print("Channel ");
        // Serial.print(i);
        // Serial.print(": ");
        // Serial.println(signed24BitData);
    }
  }
}

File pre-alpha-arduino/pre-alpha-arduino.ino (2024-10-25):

///////////////////////////// SETTINGS /////////////////////////////

// Debug
#define DEBUG true // Comment out when in operation
#define SERIAL_BAUD 115200
#if (DEBUG)
    #define DebugPrint(x) Serial.print(x)
#else
    #define DebugPrint(x)
#endif

// Options
#define SAMPLE_RATE 500


/////////////////////////////// PINS ///////////////////////////////

// DIGITAL PINS

// ANALOG PINS
#define INPUT_PIN A0

///////////////////////// GLOBAL VARIABLES /////////////////////////


//////////////////////////////////////////////////////////////////

void setup()
{
    #if (DEBUG)
        Serial.begin(SERIAL_BAUD);
        while(!Serial) {}
        DebugPrint(F("\nDEBUG MODE\n\n"));
    #endif

    pinMode(INPUT_PIN, INPUT);
}

void loop() {

	// Calculate elapsed time
	static unsigned long past = 0;
	unsigned long present = micros();
	unsigned long interval = present - past;
	past = present;

	// Run timer
	static long timer = 0;
	timer -= interval;

	// Sample
	if(timer < 0){
		timer += 1000000 / SAMPLE_RATE;
		int sensor_value = analogRead(INPUT_PIN);
		Serial.println(sensor_value);
	}
}

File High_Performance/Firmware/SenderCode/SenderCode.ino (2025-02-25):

#include <esp_now.h>
#include <WiFi.h>
#include <SPI.h>
#include <Arduino.h>
#include "SenderCode.h"

uint8_t data = 0; uint8_t data1 = 0;
uint8_t fstart = 0xA0; uint8_t fend = 0xC0;
bool start_flag = false;
bool verbose = false;
uint32_t status;
const int SAMPLES = 2;
uint8_t buffers[SAMPLES][27];
uint32_t averagedBuffer[27] = {0};
uint8_t sample = 0;

esp_now_peer_info_t slave;

void sendframe() {
  esp_now_send(slave.peer_addr, &fstart, sizeof(fstart));
  delay(1);
  for (int m = 3; m <12 ; m++) {
    esp_now_send(slave.peer_addr, (const uint8_t*)&averagedBuffer[m], sizeof(uint32_t)); 
    delay(1);
  }
  delay(1);
  esp_now_send(slave.peer_addr, &fend, sizeof(fend));
}

void setup() { 
  Serial.begin(115200);
  disableCore0WDT();
  disableCore1WDT();
  initialize(); 
  verbose = true; // When true there will be serial feedback
  WiFi.mode(WIFI_STA);
  esp_now_init();
  ScanForSlave(); 
  esp_now_add_peer(&slave);
  
  sendCommand(ADS1299_CMD_SDATAC); // Stopping continuous data mode
  delay(1);
  readAllRegisters();
  Serial.print("Updating default config");
  writeRegister(CONFIG1,0xD6); 
  writeRegister(CONFIG2,0xD0); 
  writeRegister(CONFIG3,0xEC); // BIAS buffer, internal BIAS enabled
  writeRegister(CH1SET,0x64);  
  writeRegister(CH2SET,0x64);  
  writeRegister(CH3SET,0x64);  
  writeRegister(CH4SET,0x64);  
  writeRegister(CH5SET,0x64);  
  writeRegister(CH6SET,0x64);  
  writeRegister(CH7SET,0x64);  
  writeRegister(CH8SET,0x64);  
  writeRegister(BIAS_SENSN,0xFF);
  readAllRegisters();
  delay(1);
  
  // Starting continuous data mode
  digitalWrite(CS, LOW);
  sendCommand(ADS1299_CMD_SDATAC);
  delay(1);
  sendCommand(ADS1299_CMD_RDATAC);
  delay(1);
  for (int p = 1; p <50 ; p++) {
     sendframe();
  }
  sendCommand(ADS1299_CMD_START);
  delay(1);
  digitalWrite(CS, HIGH);
  delay(1);
  Serial.print("DRDY Pin State: ");
  Serial.println(digitalRead(DRDY));
}

void loop() {
  if (digitalRead(DRDY) == LOW) {
    readADCData();
  }
  delay(20);
}

void readADCData() {
  digitalWrite(CS, LOW);  
  for (int i = 0; i < 27; i++) {
    buffers[sample][i] = SPI.transfer(0x00);  // Reading one register
  }
  digitalWrite(CS, HIGH);
  if (sample <SAMPLES) {
    sample = sample +1;
    return;
  }
  else{
    sample = 1;
  }
  
  // Averaging the captured data
  for (int i = 3; i < 27; i++) {
    for (int itr = 0; itr < SAMPLES; itr++) {
      averagedBuffer[i] += buffers[itr][i];
    }
    averagedBuffer[i] /= SAMPLES;
  }
  for (int i = 0; i < 3; i++) {
    averagedBuffer[i] = buffers[0][i];
  }
// Processing and printing the averaged data
  status = (averagedBuffer[0] << 16) | (averagedBuffer[1] << 8) | (averagedBuffer[2]);
  Serial.print("Status: 0x"); Serial.print(status, HEX); Serial.print("  ");
  sendframe();

  int32_t channelData;
  float LSB = 2.235e-5;
  float voltage;

for (int channel = 0; channel < 8; channel++) {
    channelData = (averagedBuffer[3 + channel * 3] << 16) | (averagedBuffer[4 + channel * 3] << 8) | averagedBuffer[5 + channel * 3];
    if (channelData & 0x800000) {
      channelData -= 0x1000000;
    } // Sign extension for negative values
    voltage = channelData * LSB; 
    
    if (channel == 4) {
      Serial.println();
    } 
    Serial.print("Ch "); Serial.print(channel + 1); Serial.print(": "); Serial.print(voltage, 2);
    if (channel !=8) Serial.print(", "); 
  }

  Serial.println();
}

void sendCommand(uint8_t cmd) {
  digitalWrite(CS, LOW);
  SPI.transfer(cmd);
  digitalWrite(CS, HIGH);
}
  
void start(void)
{
  sendCommand(ADS1299_CMD_RDATAC);
  delayMicroseconds(1);
  sendCommand(ADS1299_CMD_START);
  delayMicroseconds(1);
}

void readAllRegisters() {
  for (int i = 0; i < NUM_REGISTERS; i++) {
    uint8_t regValue = readRegister(i);
    if ((i == 8) | (i== 16) ){
      Serial.println();
    }
  }
  Serial.println();
}
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

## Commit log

2024-10-25 pre-alpha arduino
2024-10-25 Rename Expected Arduino IDE output.png to Expected_Arduino_IDE_output.png
2024-10-26 Created Schematic for ADS1299 Breakout Board
    [ADS1299_Breakout_Board.kicad_pcb, ADS1299_Breakout_Board.kicad_sch]
2024-10-26 Basic CAD model
    [hat.SLDASM, proto1.SLDPRT]
2024-11-12 Fixed some of the label names and started work on pcb
    [ADS1299_Breakout_Board.kicad_pcb, ADS1299_Breakout_Board.kicad_sch]
2024-11-14 Finished up traces
    [ADS1299_Breakout_Board.kicad_pcb, ADS1299_Breakout_Board.kicad_sch]
2024-11-15 Created gerber files and added component libraries
    [ADS1299IPAG.step, ADS1299_Breakout_Board-B_Cu.gbr, ADS1299_Breakout_Board-B_Mask.gbr, ADS1299_Breakout_Board-B_Paste.gbr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]
2024-11-15 Linked libraries to project
    [ADS1299IPAG.step, ADS1299_Breakout_Board-B_Cu.gbr, ADS1299_Breakout_Board-B_Mask.gbr, ADS1299_Breakout_Board-B_Paste.gbr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]
2024-11-15 Linked Footprint libraries
    [ADS1299_Breakout_Board.kicad_sch]
2024-11-15 Added 3d model to pcblayout
    [ADS1299_Breakout_Board.kicad_pcb]
2024-11-19 Electrode Model + Components List
    [Components to be ordered.xlsx, conductive electrode-short finger-not ours.SLDPRT, conductive electrode-short finger-not ours.stl, electrode.SLDPRT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]
2024-11-19 Update PCB Schematic
    [PCBSchematic.kicad_sch]
2024-11-21 Updated code for ESP32C6 BLE connection with laptop
2024-12-02 Update code
    [input_data.csv]
2025-01-31 Update eeg headset
    [electrode_holder.STL, fastening_screw.STL, hexagonal_fitting.STL, medium_headset_back_half.stl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]
2025-02-01 new GUI framework
2025-02-12 new additions
    added ADS1299 library to esp32 folder and gui can connect with ble to esp32
2025-02-13 More Electrode work, Start of Muxed PCB
    [Muxed_ADC_PCB.kicad_pcb, Muxed_ADC_PCB.kicad_sch, electrode_holder.STL, electrode_screw.SLDPRT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]
2025-02-21 esp32 sketches with ads1299 library
2025-02-25 repo organization
    [ADS1299IPAG.step, ADS1299_Breakout_Board-B_Cu.gbr, ADS1299_Breakout_Board-B_Mask.gbr, ADS1299_Breakout_Board-B_Paste.gbr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]
2025-03-10 Archived in favor of combined pcb
    [ADS1299_PCB_Final.kicad_pcb, ADS1299_PCB_Final.kicad_sch, ADS1299_PCB_Final.sch, MCP1640.step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]
2025-03-10 Final combined ppcb
    [Combined_PCB.kicad_pcb, Combined_PCB.kicad_sch, Combined_PCB.sch, MCP1640.step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]
2025-03-13 Semi-finalized PCB Layout final
    [adc_microcontroller.kicad_sch, inputs_filtering.kicad_sch]
2025-03-13 Schematic and footprints complete
    [ADS1299IPAG.step, LSM6DSOX.step, MCP1640.step, W3A45C102K4T2A.step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]
2025-03-15 ADS1299 final pcb layout done (hopefully)
    [Combined_PCB.kicad_pcb, adc_microcontroller.kicad_sch, inputs_filtering.kicad_sch]
2025-03-18 Add CS
    [Combined_PCB-B_Mask.gbr, Combined_PCB-B_Silkscreen.gbr, Combined_PCB-Back.gbr, Combined_PCB-Edge_Cuts.gbr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]
2025-03-25 Final PCB Render Done
    [Combined_PCB.kicad_pcb, Combined_PCB.step, adc_microcontroller.kicad_sch]
2025-03-28 Preliminary housing CAD
    [Combined_PCB.SLDASM, Housing.SLDASM, Housing.SLDPRT]
2025-03-29 Reorganized Balanced Performance
    [ADS1299IPAG.step, Combined_PCB-B_Mask.gbr, Combined_PCB-B_Silkscreen.gbr, Combined_PCB-Back.gbr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]
2025-03-29 added pcb images
2025-03-29 organizing folders
    [ADS1299IPAG.step, ADS1299_Breakout_Board-B_Cu.gbr, ADS1299_Breakout_Board-B_Mask.gbr, ADS1299_Breakout_Board-B_Paste.gbr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]
2025-03-29 More folder organization
    [conductive electrode-short finger-not ours.SLDPRT, conductive electrode-short finger-not ours.stl, electrode.SLDPRT, electrode.STL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]
2025-03-29 More folder stuff
    [real_time_data.csv]
2025-03-29 Final folder stuff
    [ADS1299IPAG.step, ADS1299_Breakout_Board-B_Cu.gbr, ADS1299_Breakout_Board-B_Mask.gbr, ADS1299_Breakout_Board-B_Paste.gbr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]
2025-04-01 Update ESP32
2025-04-02 V2 Housing
    [Housing.SLDASM, Housing.SLDPRT, Housing_bot.STL, Housing_top.STL]
2025-04-03 Fix sample timing
2025-04-10 Add images of breakout board
2025-04-14 Created CAD for breakout board housing
    [ADS1299_Breakout_Board.SLDASM, ADS1299_Breakout_Board.step, ADS1299_Breakout_Board_Housing.SLDASM, ADS1299_Breakout_Board_Housing.SLDPRT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]
